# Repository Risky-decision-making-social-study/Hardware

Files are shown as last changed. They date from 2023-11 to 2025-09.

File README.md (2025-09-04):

# Hardware

This repository contains the design files and documentation for the "How does social context modulate risky decision-making in long-tailed macaques (Macaca fascicularis)? A research report on problematic issues with a repeated sampling from experience paradigm" project.

Fancy-Drawing

## Publication



## Online Viewer

You can view the design files in your browser using the online viewer.

<https://a360.co/31DxOK0>

## Manufacturing

The files for manufacturing can be found in the following folders:

+ STL/: Contains the STL files for 3D printing the parts.
+ Panels/: Contains the files for cutting the panels.
+ PDF/: Contains the files with specifications, turning and assembly instructions.

Alternatively, you can export all parts from the provided full assemblies with either the `ApparatusAssembly.step` or `ApparatusAssembly.f3z` files.

## Concept

For further discussion about the individual parts and modules, read the concept and implementation descriptions in the [concept folder](Concept/README.md).

## Bill of Materials

For a list of parts used in the construction of the Apparatuses in this project and a cost estimation, look at the [BOM.md file](BOM.md).

## License

This project is licensed under the MIT License - see the LICENSE.md file for details.

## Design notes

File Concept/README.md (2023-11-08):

# Hardware concept

## Carousel

The carousel is the component that is responsible for the reward distribution. Mechanically, the carousel is driven by a stepper motor that is connected to the carousel assembly via a gear train with a ratio of 18:5. This allows the motor to achieve an accuracy of 0.5° without microstepping when rotating the carousel, as calculated in [Table 1](#table_1). In addition, the carousel is equipped with an absolute magnetic encoder which allows it to determine the current absolute position of the carousel at any time after a one-time calibration. The encoder is located on the underside of the carrier plate and is mounted according to the data sheet of the AS5048A which is used in this application. Except for the mount plate, the carousel consists of only 3D-printed parts and is designed for production using the FDM printing process.

carousel figures

*Figure 1: Concept*

| Steps-Rotation                | Carousel |
| ----------------------------- | -------- |
| Compartments per Rotation     | 16       |
| Angle per Compartment         | 22,5°    |
| Gear Carousel Teeth           | 180      |
| Gear Stepper Teeth            | 50       |
| Stepper Angle per Compartment | 81°      |
| Stepper StepAngle             | 1,8°     |
| Steps per Compartment         | 45       |

*Table 1: Steps and rotational calculations of the square*

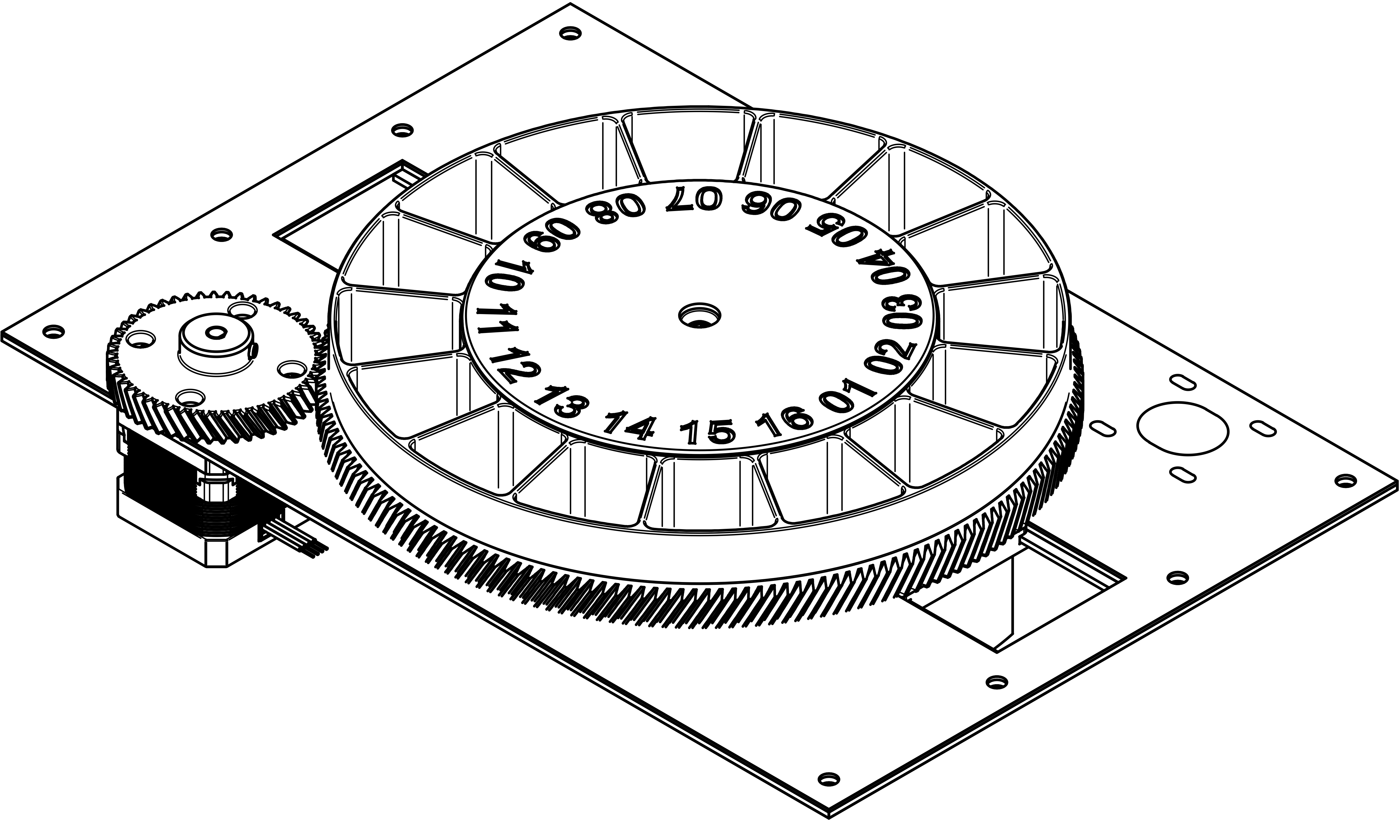
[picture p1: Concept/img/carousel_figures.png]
carousel figures


*Figure 2: Final Drawing*

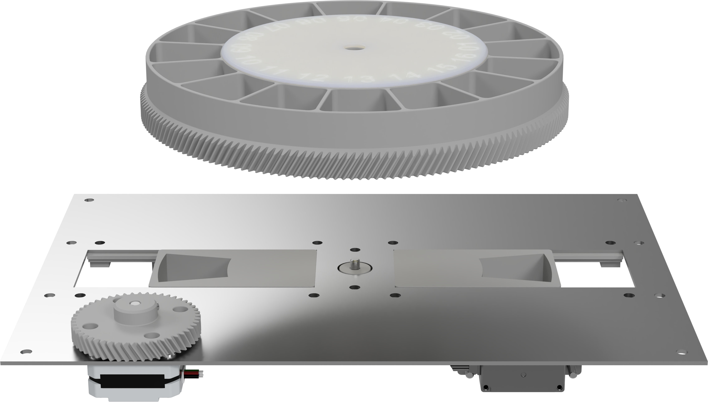
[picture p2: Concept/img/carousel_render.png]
carousel render


*Figure 3: Final Render*

## Frame

The main structure of the apparatuses is constructed out of aluminum extrusions, which allows for changes to the structure later on and are very easy to assemble. Additionally, they are very durable, which is a big advantage for a portable piece of hardware like this, as it can support the panels, allowing for weight savings on the paneling and even allows the apparatus to survive drops with ease.

fram_frame

*Figure 4: Frame*

## Lights

The illumination of the apparatuses is done by LED strips. A addressable lighting system based on addressable LEDs. Examples of the individual LED components are WS2812B, SK9822 and APA102C. These LED components are commonly sold as LED strips by the meter, which are suitable for use directly behind a diffuser, like the outer wall of the apparatuses, as shown in [Figure 5](#figure_5). In this concept, the signal light can be controlled virtually via the status light. For this purpose, a part of the status light LED strips is placed in a delimited area on the inside of the diffuser near the lever and switched on and off independently of the rest of the strip. The color of the signal light can also be changed afterwards.

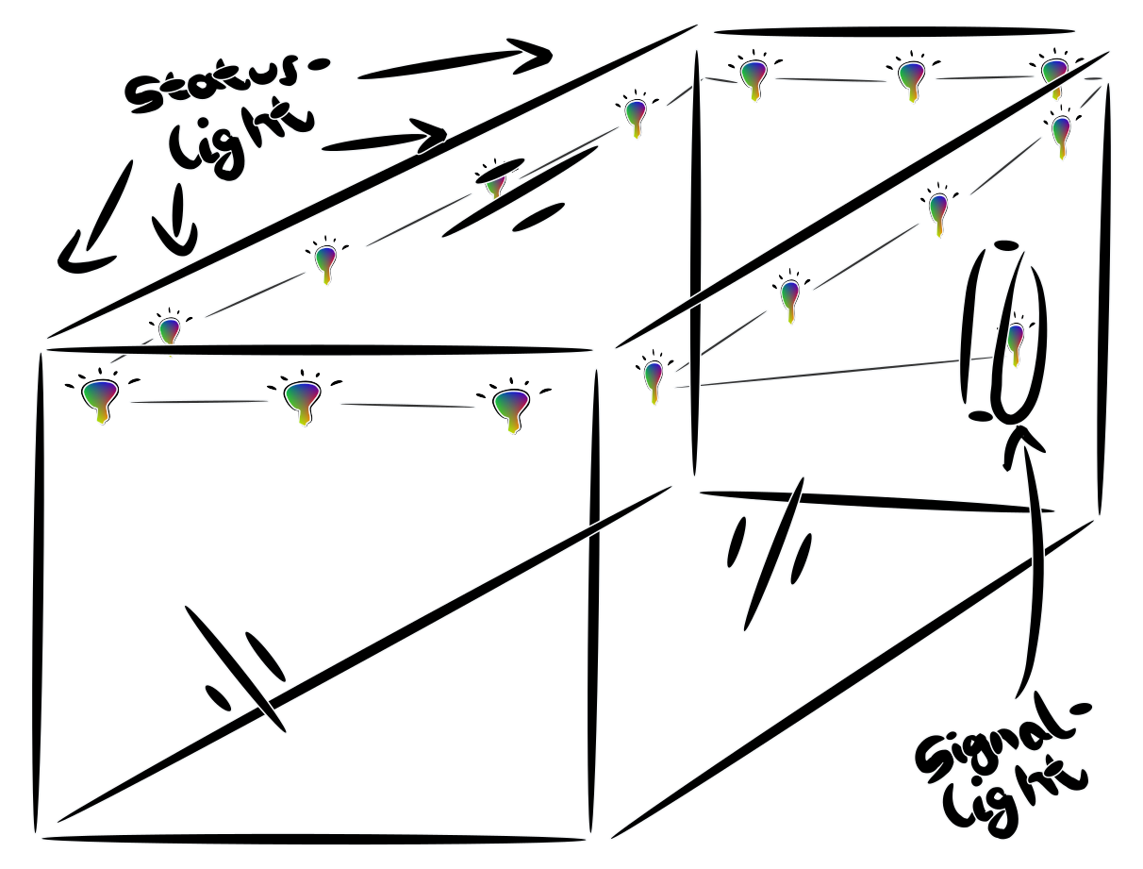
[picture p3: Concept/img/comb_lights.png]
comb_lights


*Figure 5: Lights*

## Lever

The lever is, as can be seen in [Figure 7](#figure_7), the mechanically most complex individual component of the apparatuses. It has a motorized locking system that prevents the lever from moving downward. It also has three sensors that detect touch, the states of the lever being fully pulled or fully up position. In addition, large parts of the lever are made of metal to withstand the mechanical stresses that occur when the lever is pulled by the subjects. These include the lever rod, the joint axis, and the parts of the locking device: ratchet wheel and pawl. In addition, a spring located in the lower part of the assembly ensures that the lever returns to the fully up position when no force is applied. Unfortunately, the lever is the most difficult to manufacture, as due to the high mechanical and environmental stress of the components, they have to be machined or cut out of stainless steel.

lever_ratchet

*Figure 6: Lever concept*

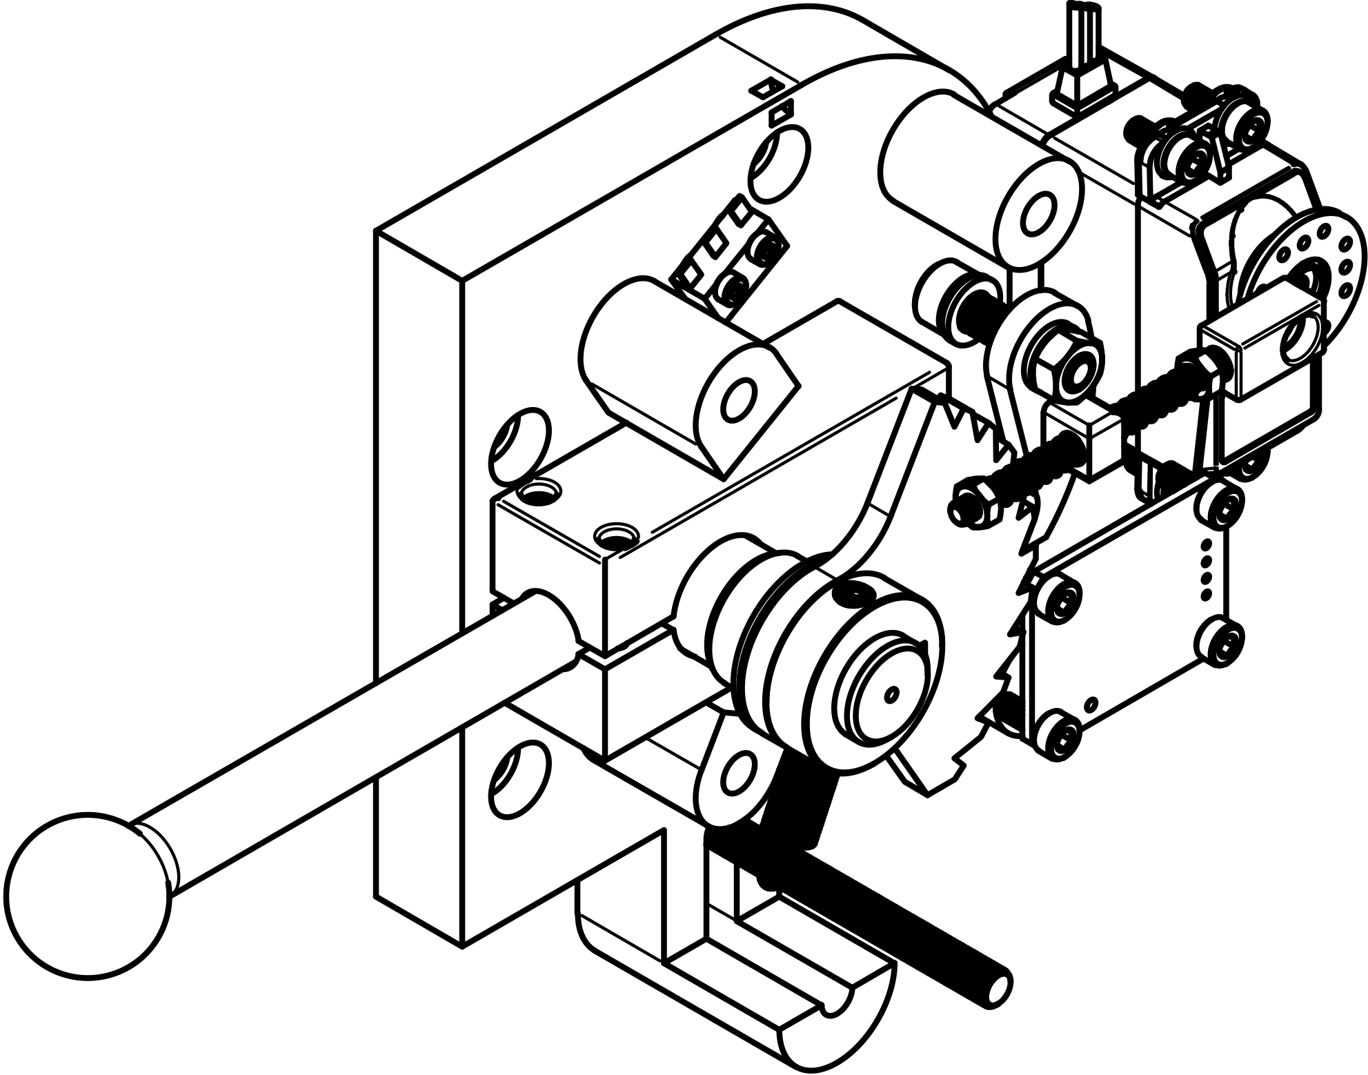
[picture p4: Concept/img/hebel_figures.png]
hebel_figures


*Figure 7: Open lever*

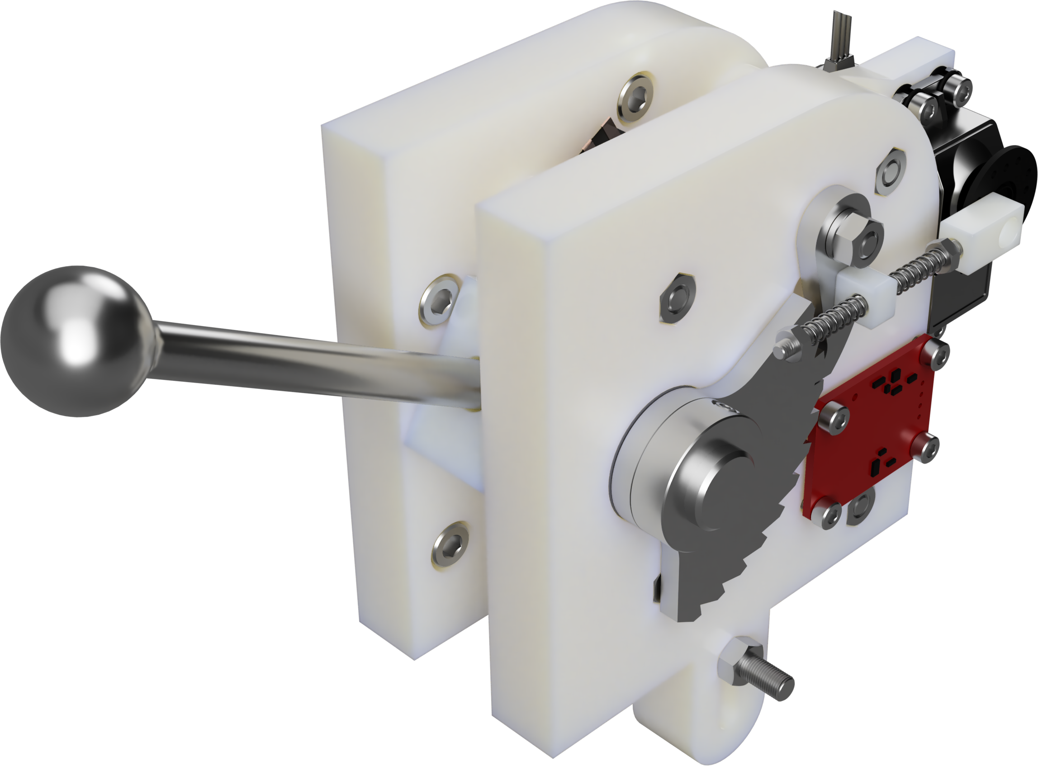
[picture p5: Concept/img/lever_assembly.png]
lever_assembly


*Figure 8: Render lever*

apparatus lever render

*Figure 9: Render lever in the apparatus*

## Hopper

The most important aspect when delivering rewards is the safety of the test subjects. For this reason, special care was taken in the design to ensure that the test subjects could not reach into the mechanical parts of the device. [Figure 10](#figure_10) shows the conceptual cross-section of the reward slide the test subjects interact with. The smallest distance between the walls is chosen so that a standard grape with an estimated maximum diameter of up to 20 mm can still fit through, but due to the chosen path that the reward must take through the chute, it is made as difficult as possible to reach around it. The 20 mm grape is an upper size estimate that was chosen to take into account most of the possible reward types available to the researchers.

Reward_chute_locked

*Figure 10: Concept of a monkey proof reward chute*

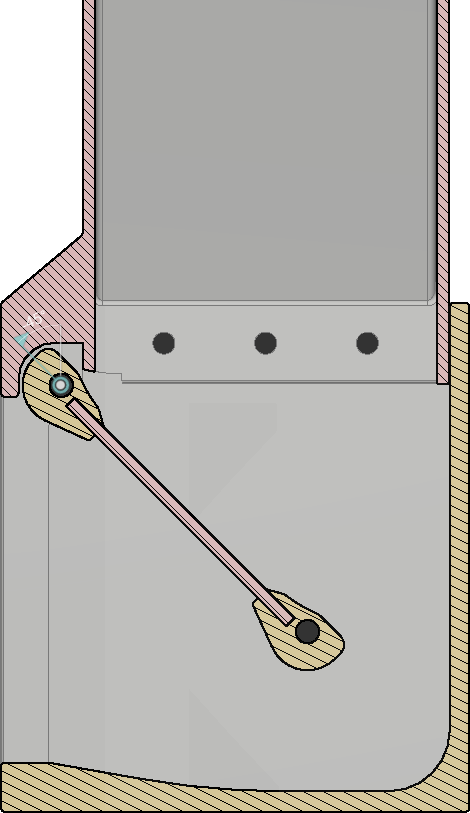
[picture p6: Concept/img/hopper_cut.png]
hopper_cut


*Figure 11: Section analysis of the final design*

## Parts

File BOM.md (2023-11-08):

| #   | Part Name                                                                                                                                                                      | Type / length mm                                                                                  | Number for two apparatuses | Estimated total amount for two apparatuses |
| --- | ------------------------------------------------------------------------------------------------------------------------------------------------------------------------------ | ------------------------------------------------------------------------------------------------- | -------------------------- | ------------------------------------------ |
| 1   | Grooved ball bearing                                                                                                                                                           | 8x16x5                                                                                            | 4                          | 0,00 €                                     |
| 2   | Screw DIN EN ISO 7380 - Pan head screw                                                                                                                                         | M2x5                                                                                              | 4                          | 0,00 €                                     |
| 3   | HAWA 1008234 Kaltgeräte Anschlusskabel Schwarz 5.00 m                                                                                                                          | Power cable                                                                                       | 2                          | 0,00 €                                     |
| 4   | LOCTITE 243 Medium Strength Threadlocker Adhesive Glue 50ml Bottle                                                                                                             | Screw locking varnish                                                                             | 2                          | 36,08 €                                    |
| 5   | ruthex Threaded Insert, Brass Threaded Bushings                                                                                                                                | 3D printing thread inserts                                                                        | 1                          | 27,99 €                                    |
| 6   | Nema 17 Bipolar 1.8deg 16Ncm (22.6oz.in) 1A 3.7V 42x42x20mm 4 Wires                                                                                                            | 17HS08-1004S                                                                                      | 6                          | 65,94 €                                    |
| 7   | BTF-LIGHTING SK9822 (similar to APA102C) Individually Addressable 16.5ft 5m 60 Pixels/LEDs/m 300 LEDs IP30 Non-Waterproof Black PCB Data and Clock Separately DC5V Full Colour | 5m (for both apparatuses)                                                                         | 1                          | 65,99 €                                    |
| 8   | 14-bit Magnetic Rotary Encoder IC                                                                                                                                              | AS5048                                                                                            | 4                          | 56,68 €                                    |
| 9   | Servo 180deg                                                                                                                                                                   | ROB-11965                                                                                         | 10                         | 109,50 €                                   |
| 10  | TMC2209 SILENTSTEPSTICK                                                                                                                                                        | (empty)                                                                                           | 12                         | 149,04 €                                   |
| 11  | DC Step Down Converter Buck Voltage Regulator 18-72V to 5V 6A 30W                                                                                                              | LED Voltage Supply                                                                                | 2                          | 46,50 €                                    |
| 12  | GST90A24-P1M                                                                                                                                                                   | AC/DC unit                                                                                        | 2                          | 56,36 €                                    |
| 13  | 1803277                                                                                                                                                                        | J2.1                                                                                              | 6                          | 4,20 €                                     |
| 14  | 1803578                                                                                                                                                                        | J2.2                                                                                              | 6                          | 12,18 €                                    |
| 15  | 12063A822JAT2A                                                                                                                                                                 | C5                                                                                                | 18                         | 8,28 €                                     |
| 16  | C3225X7R1H106M250AC                                                                                                                                                            | C2, C10                                                                                           | 8                          | 6,32 €                                     |
| 17  |                                                                                                                                                                                | C2, C10                                                                                           | 14                         | 11,06 €                                    |
| 18  | CC0805KRX7R7BB104                                                                                                                                                              | C6, C9                                                                                            | 8                          | 0,80 €                                     |
| 19  |                                                                                                                                                                                | C6, C9                                                                                            | 14                         | 1,40 €                                     |
| 20  | CG0603MLC-05LE                                                                                                                                                                 | D3                                                                                                | 6                          | 1,98 €                                     |
| 21  | CG0603MLC-24LE                                                                                                                                                                 | D2                                                                                                | 6                          | 1,98 €                                     |
| 22  |                                                                                                                                                                                | D2                                                                                                | 12                         | 3,84 €                                     |
| 23  | CG0603MLC-3.3LE                                                                                                                                                                | D4-D15                                                                                            | 28                         | 9,24 €                                     |
| 24  |                                                                                                                                                                                | D4, D5, D6, D7, D8, D9, D10, D11, D12, D13, D14, D15, D16, D17, D18, D19, D20, D21, D22, D23, D24 | 62                         | 13,04 €                                    |
| 25  | CL21A106KQCLRNC                                                                                                                                                                | C1                                                                                                | 18                         | 1,62 €                                     |
| 26  | CL21B105KOFNNNG                                                                                                                                                                | C8                                                                                                | 18                         | 1,44 €                                     |
| 27  | CL21C100JBANNNC                                                                                                                                                                | C3                                                                                                | 18                         | 1,44 €                                     |
| 28  | CRCW080510K0FKEAC                                                                                                                                                              | R3, R4                                                                                            | 8                          | 0,64 €                                     |
| 29  |                                                                                                                                                                                | R3, R4, R16, R21, R22, R25, R26                                                                   | 24                         | 1,92 €                                     |
| 30  | CRCW080510K2FKEA                                                                                                                                                               | R14                                                                                               | 18                         | 1,44 €                                     |
| 31  | CRCW08051K96FKEA                                                                                                                                                               | R15                                                                                               | 18                         | 1,44 €                                     |
| 32  | CRCW0805220RFKEAC                                                                                                                                                              | R5-R10                                                                                            | 16                         | 1,28 €                                     |
| 33  |                                                                                                                                                                                | R5, R6, R7, R8, R9, R10, R11, R12, R17, R18, R19, R20                                             | 34                         | 2,72 €                                     |
| 34  | CRCW08054K70FKEAC                                                                                                                                                              | R1, R2                                                                                            | 8                          | 0,64 €                                     |
| 35  |                                                                                                                                                                                | R1, R2                                                                                            | 14                         | 1,12 €                                     |
| 36  | CRCW080560K4FKEA                                                                                                                                                               | R13                                                                                               | 18                         | 1,44 €                                     |
| 37  | GRM2165C1H102JA01J                                                                                                                                                             | C4                                                                                                | 18                         | 2,52 €                                     |
| 38  | GRM32ER61C476KE15L                                                                                                                                                             | C7, C11, C12                                                                                      | 10                         | 9,60 €                                     |
| 39  |                                                                                                                                                                                | C7, C11, C12                                                                                      | 6                          | 5,76 €                                     |
| 40  | NCP164CSN330T1G                                                                                                                                                                | U3                                                                                                | 8                          | 4,16 €                                     |
| 41  | PCA9685PW,118                                                                                                                                                                  | U1                                                                                                | 8                          | 15,28 €                                    |
| 42  | PRT-14017                                                                                                                                                                      | J1                                                                                                | 8                          | 13,20 €                                    |
| 43  | SBRD10200TR                                                                                                                                                                    | D1                                                                                                | 8                          | 3,20 €                                     |
| 44  | TPS54531DDAR                                                                                                                                                                   | U2                                                                                                | 8                          | 10,56 €                                    |
| 45  | TSW-150-07-T-S                                                                                                                                                                 | J3-J14                                                                                            | 8                          | 16,16 €                                    |
| 46  | Omron Electronics Inc-EMC Div D2F-5L                                                                                                                                           | Microswitch                                                                                       | 4                          | 9,44 €                                     |
| 47  | DIN 35 – Hutschiene                                                                                                                                                            | 35x220mm                                                                                          | 2                          | 36,50 €                                    |
| 48  | EHRJ45P6S                                                                                                                                                                      | RJ45 Panel Mount                                                                                  | 2                          | 21,48 €                                    |
| 49  | PJ-065B                                                                                                                                                                        | Connector Panel ID 2,50mm, AD 5,50mm, L 10.70mm                                                   | 4                          | 7,28 €                                     |
| 50  | SEN-12041                                                                                                                                                                      | Chip: capacitive sensor                                                                           | 3                          | 17,61 €                                    |
| 51  | 150080RS75000                                                                                                                                                                  | D25                                                                                               | 12                         | 1,80 €                                     |
| 52  | CG0603MLC-05E                                                                                                                                                                  | D3                                                                                                | 12                         | 4,80 €                                     |
| 53  | CRCW0603100RFKEAC                                                                                                                                                              | R23, R24, R27, R28, R29, R30                                                                      | 22                         | 1,76 €                                     |
| 54  | EEE-FT1V101AP                                                                                                                                                                  | C13, C14                                                                                          | 14                         | 5,88 €                                     |
| 55  | RC0805FR-0749R9L                                                                                                                                                               | R31                                                                                               | 12                         | 0,96 €                                     |
| 56  | CL10B103KB8NNNC                                                                                                                                                                | C15, C16                                                                                          | 12                         | 0,96 €                                     |
| 57  | SN74LVC2T45DCUR                                                                                                                                                                | U4                                                                                                | 4                          | 1,92 €                                     |
| 58  | Trägerplatte (Alu/Pertinax)                                                                                                                                                    | 320x220x3                                                                                         | 4                          | 0,00 €                                     |
| 59  | Aluprofil 20x20 I-Typ Nut 5                                                                                                                                                    | 280 mm                                                                                            | 14                         | 12,76 €                                    |
| 60  |                                                                                                                                                                                | 320 mm                                                                                            | 8                          | 8,33 €                                     |
| 61  |                                                                                                                                                                                | 490mm                                                                                             | 12                         | 19,14 €                                    |
| 62  |                                                                                                                                                                                | 225 mm                                                                                            | 8                          | 5,86 €                                     |
| 63  | Nutenstein mit Steg I-Typ Nut 5 {[}M5{]}                                                                                                                                       | M5                                                                                                | 540                        | 98,06 €                                    |
| 64  | Schraube DIN EN ISO 7380 - Linsenkopfschraube                                                                                                                                  | M3x8                                                                                              | 16                         | 3,08 €                                     |
| 65  |                                                                                                                                                                                | M4x8                                                                                              | 32                         | 12,47 €                                    |
| 66  |                                                                                                                                                                                | M5x16                                                                                             | 48                         | 18,70 €                                    |
| 67  |                                                                                                                                                                                | M5x35                                                                                             | 4                          | 1,56 €                                     |
| 68  |                                                                                                                                                                                | M5x8                                                                                              | 70                         | 27,27 €                                    |
| 69  | Igus Gleitlager mit Bund GFM-1618-09                                                                                                                                           | Slide bearing                                                                                     | 6                          | 14,66 €                                    |
| 70  | Präzisionswelle Stahl Ø16mm                                                                                                                                                    | 500 mm                                                                                            | 1                          | 3,23 €                                     |
| 71  | Senkschraube mit Innensechskant nach DIN 7991                                                                                                                                  | M5x16                                                                                             | 6                          | 2,34 €                                     |
| 72  | M5 Gewindestange DIN 976 Stahl, 1000mm                                                                                                                                         | Threaded rod                                                                                      | 1                          | 1,19 €                                     |
| 73  | Mutter DIN 934                                                                                                                                                                 | M5                                                                                                | 16                         | 4,72 €                                     |
| 74  | Stahlwinkel 20 verzinkt                                                                                                                                                        | 20x20 mm                                                                                          | 36                         | 36,11 €                                    |
| 75  | Gewindestange   60mm                                                                                                                                                           | M5                                                                                                | 2                          |                                            |
| 76  | XAL6060-562MEB                                                                                                                                                                 | L1                                                                                                | 6                          | 15,00 €                                    |
| 77  | Raspberry Pi RPI4-MODBP-4GB-BULK                                                                                                                                               | Single Board Computer                                                                             | 2                          | 117,50 €                                   |
| 78  | Digitus RJ45 Network cable, patch cable CAT 5e SF/UTP 0.50 m Green                                                                                                             | 0.5m Patch Cable                                                                                  | 4                          | 11,96 €                                    |
| 79  | Renkforce RJ45 Network cable, patch cable CAT 6A S/FTP 10.00 m Grey ultra flexible, gold plated connectors                                                                     | 10m Patch Cable                                                                                   | 2                          | 37,98 €                                    |
| 80  | TP-LINK Network switch 5 ports                                                                                                                                                 | NetworkSwitch                                                                                     | 1                          | 21,99 €                                    |
| 81  | Ultimaker Filament PA (Polyamid) 2.85 mm Schwarz 750 g                                                                                                                         | 3D printing Nylon                                                                                 | 2                          | 126,62 €                                   |
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

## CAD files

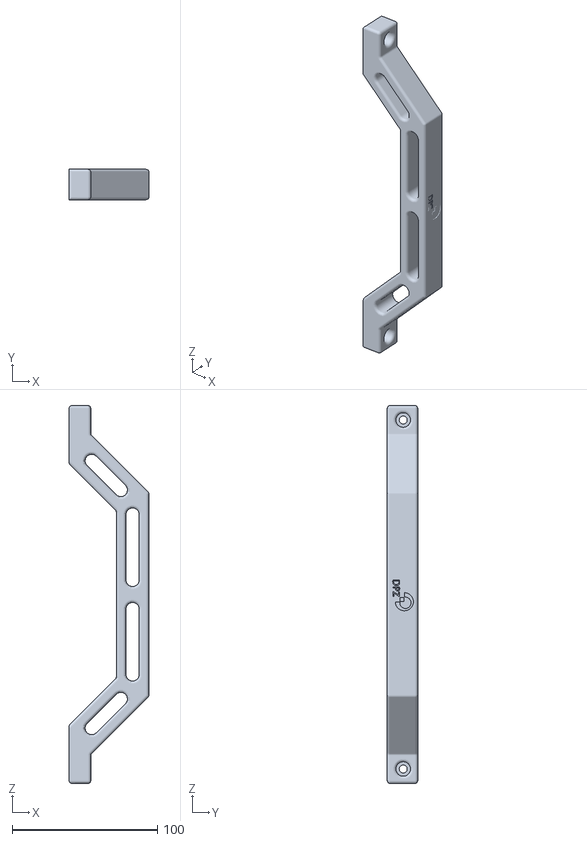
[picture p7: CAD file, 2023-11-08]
STL/AparatusAssembly_Handle.stl
55.0 x 21.0 x 260.0

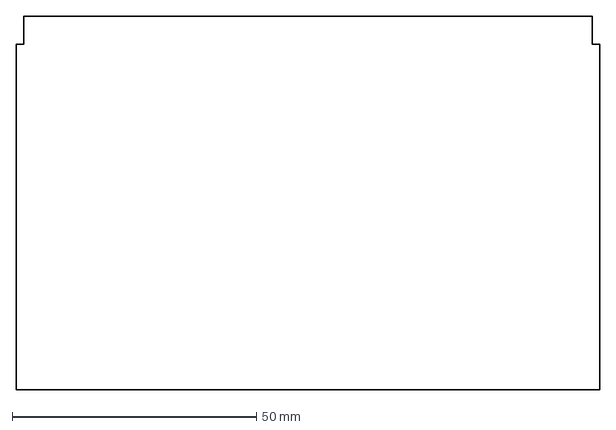
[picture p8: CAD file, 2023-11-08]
STL/ApparatusAssembly_Hopper/ApparatusAssembly_Hopper_Door_Short.dxf
119.5 x 76.5 mm

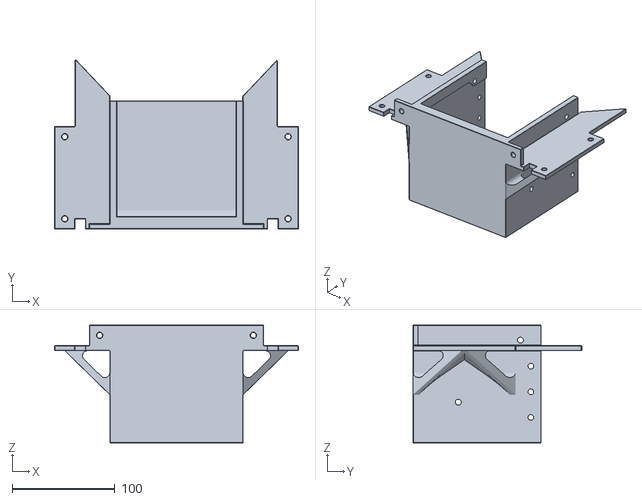
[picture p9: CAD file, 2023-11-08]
STL/ApparatusAssembly_Hopper/BottomPart.stl
238.0 x 164.9 x 115.0

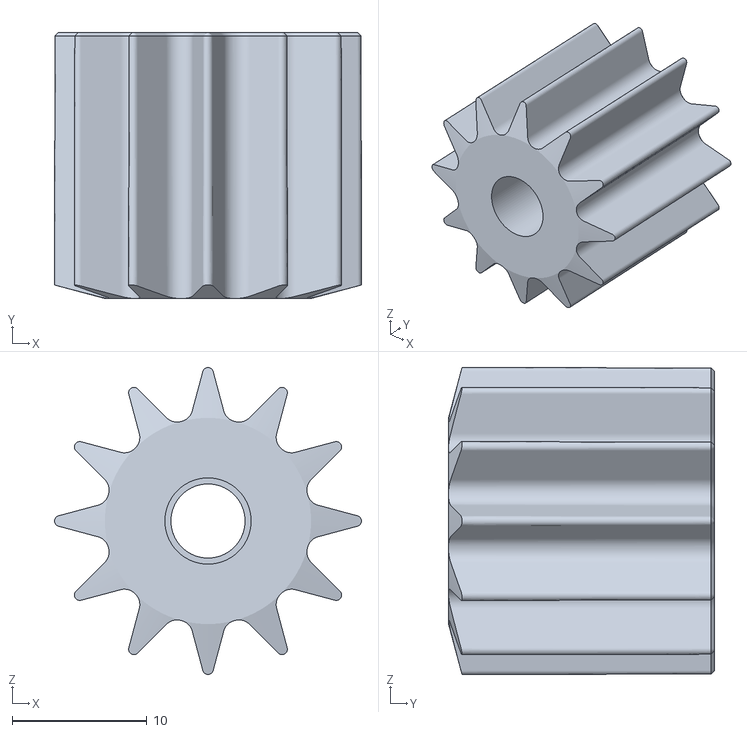
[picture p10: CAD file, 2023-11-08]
STL/Carousel_Assembly/Carousel_RotaryAssembly/Attacher.stl
22.8 x 19.8 x 22.8

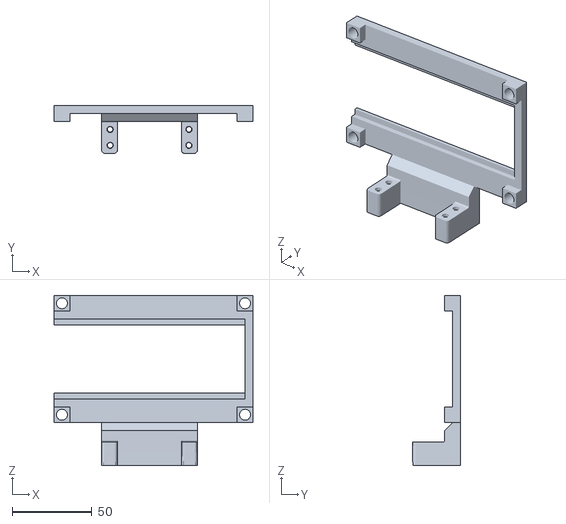
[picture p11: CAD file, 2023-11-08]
STL/Carousel_Assembly/Carousel_sliding-door/Rail.stl
125.0 x 30.0 x 107.0

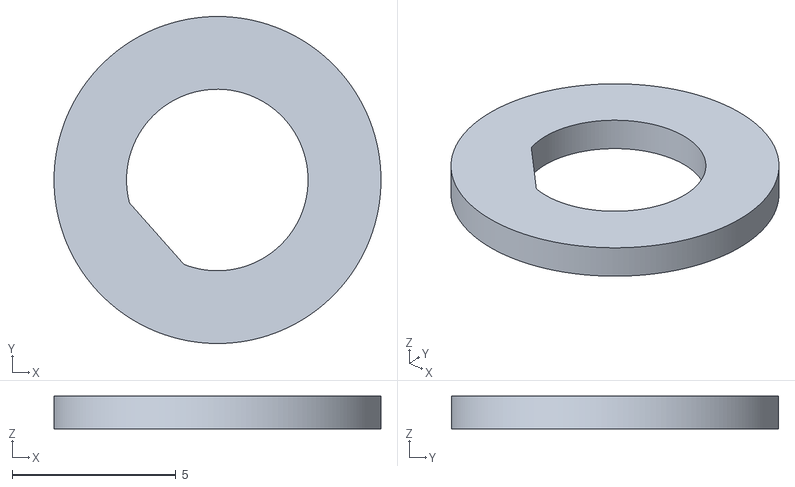
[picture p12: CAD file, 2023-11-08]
STL/Carousel_Assembly/Carousel_StepperAssembly/Spacer.stl
10.00 x 10.00 x 1.00

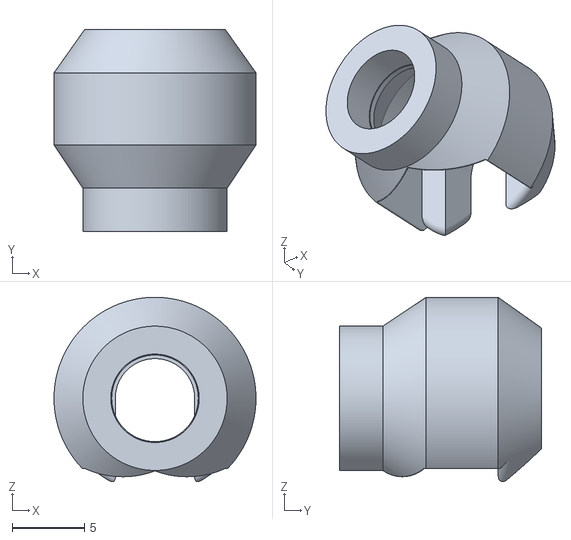
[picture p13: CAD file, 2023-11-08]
STL/Carousel_Assembly/MagnetMount.stl
14.0 x 14.0 x 12.8

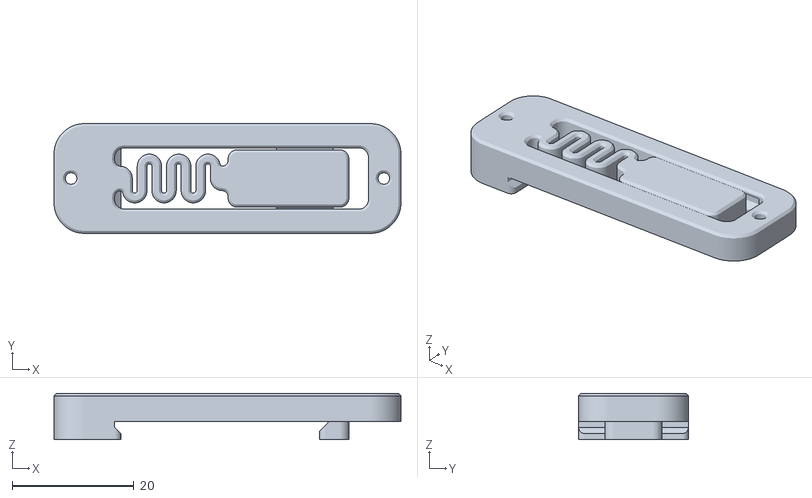
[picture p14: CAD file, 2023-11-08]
STL/ElectronicsRail/BracketRailMount.stl
56.9 x 18.0 x 7.60

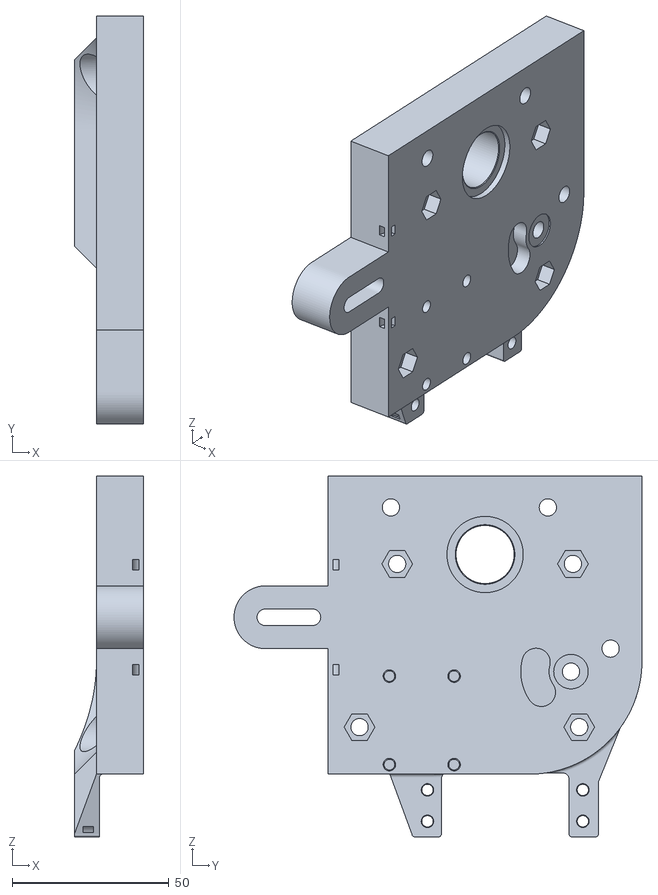
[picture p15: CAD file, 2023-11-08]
STL/LeverAssembly/Housing/Hebel_Plate_R.stl
22.0 x 130.0 x 115.0

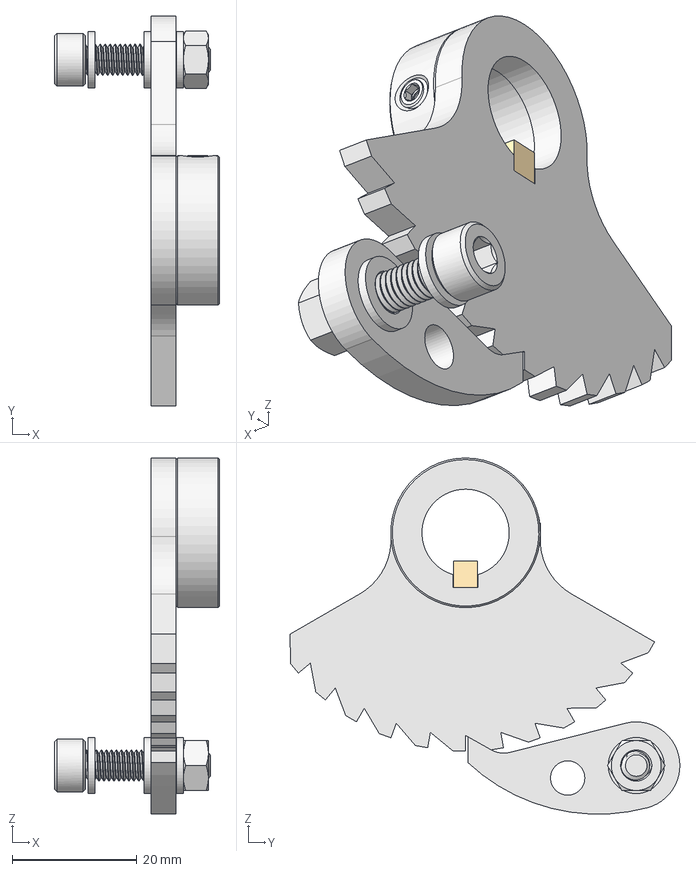
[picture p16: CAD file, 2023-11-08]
STL/LeverAssembly/KlinkenSperrung.step
26.5 x 62.5 x 57.1 mm
Sperrad
Klinke
Passfeder
M4x5 - DIN 914 - 91217A110
M5x20 - DIN 912 - 91292A128
M5 Nut - DIN 934 - 91828A241
MessingLager
M5x1mm OD 9mm Washer - DIN433 - 98690A112 x 3

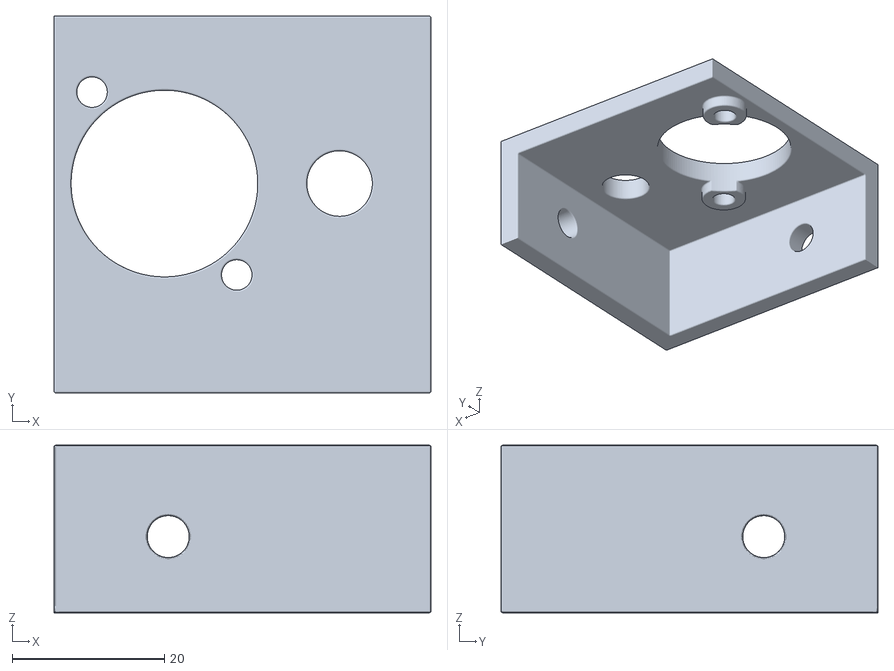
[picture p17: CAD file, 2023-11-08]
STL/PlugInterface.stl
49.5 x 49.5 x 22.0

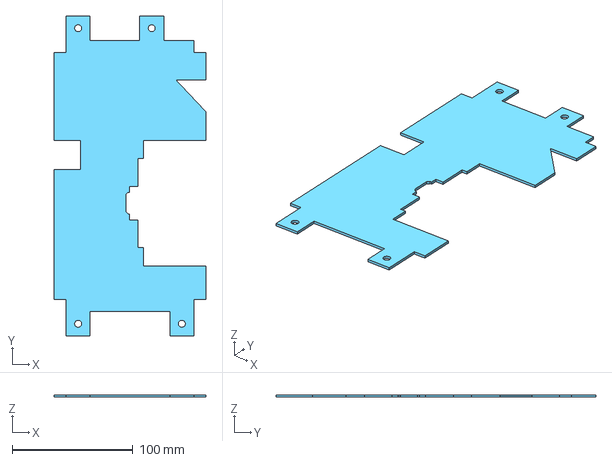
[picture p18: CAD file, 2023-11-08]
Panels/FrontInnerSide_Lever.step
126.0 x 265.0 x 2.00 mm

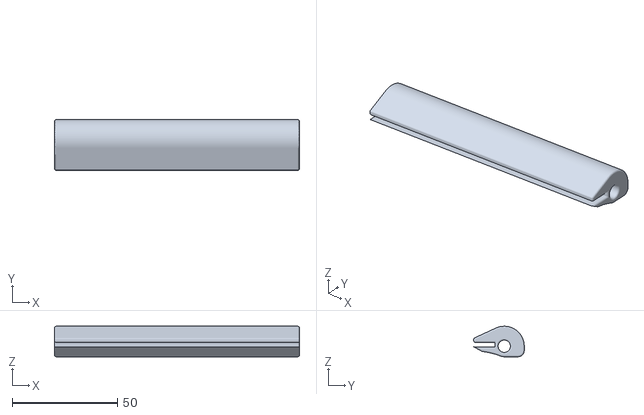
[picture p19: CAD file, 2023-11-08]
STL/ApparatusAssembly_Hopper/Hinge.stl
116.2 x 24.0 x 14.5

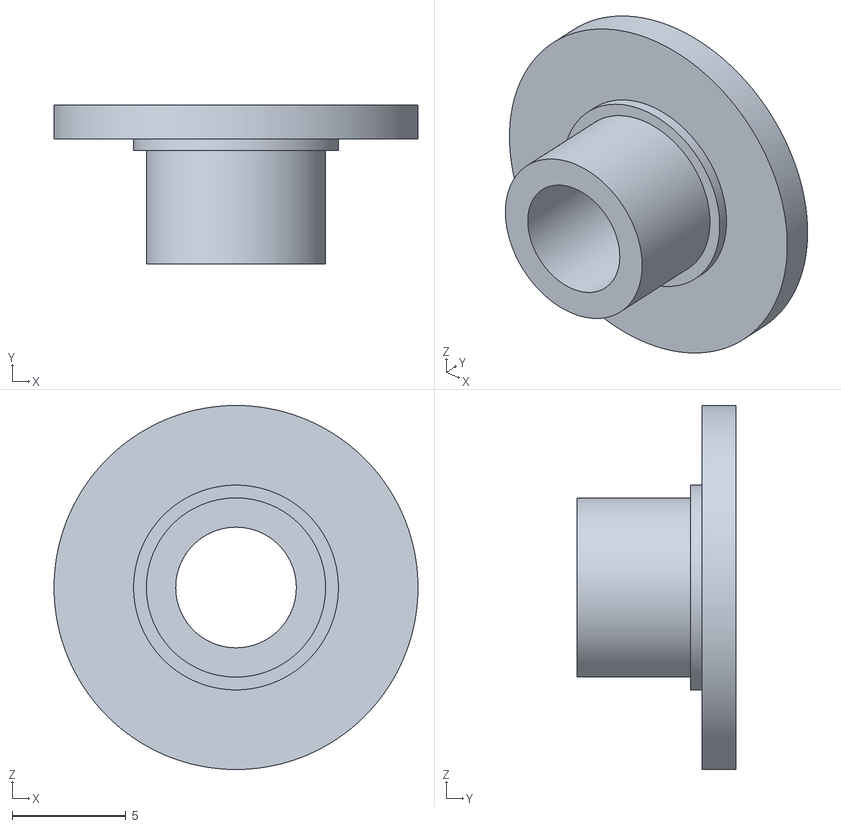
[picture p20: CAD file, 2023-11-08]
STL/Carousel_Assembly/AxisTranslator.stl
16.0 x 7.00 x 16.0

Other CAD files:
Panels/FrontOuterHuman.step
STL/Carousel_Assembly/Carousel_sliding-door/Car.stl
STL/ElectronicsRail/RPIBracket.stl
STL/Feet(Mirror).stl
Panels/Carousel_MountPlate.dxf
Panels/Carousel_MountPlate.step
Panels/FontInnerSide.step
Panels/FrontInnerSide.dxf
Panels/FrontInnerSide_Electric.dxf
Panels/FrontInnerSide_Electric.step
Panels/FrontInnerSide_Lever.dxf
Panels/FrontOuterHuman.dxf
Panels/FrontOuterMonkey.dxf
Panels/FrontOuterMonkey.step
Panels/FrontTopInner.dxf
Panels/FrontTopInner.step
Panels/ProtectionPanel.dxf
Panels/ProtectionPanel.step
Panels/SideInner.dxf
Panels/SideInner.step
Panels/SideOuter.dxf
Panels/SideOuter.step
Panels/TopBottomOuter.dxf
Panels/TopBottomOuter.step
STL/ApparatusAssembly_Hopper/Cover.stl
STL/ApparatusAssembly_Hopper/TopPart.stl
STL/Carousel_Assembly/Carousel_Joint.stl
STL/Carousel_Assembly/Carousel_sliding-door/Spur Gear (25 teeth).stl
STL/Feet.stl
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

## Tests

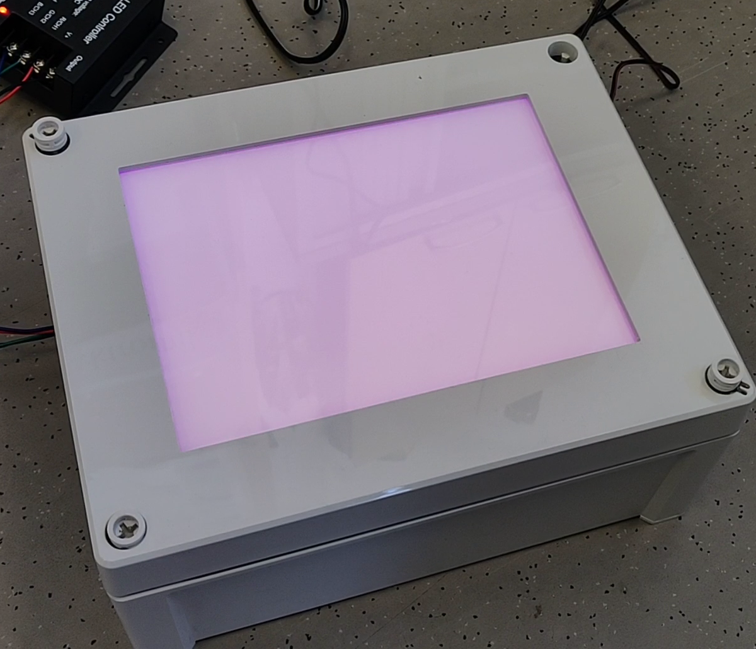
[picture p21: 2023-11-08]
Concept/img/LightTest/LightTest_02.png

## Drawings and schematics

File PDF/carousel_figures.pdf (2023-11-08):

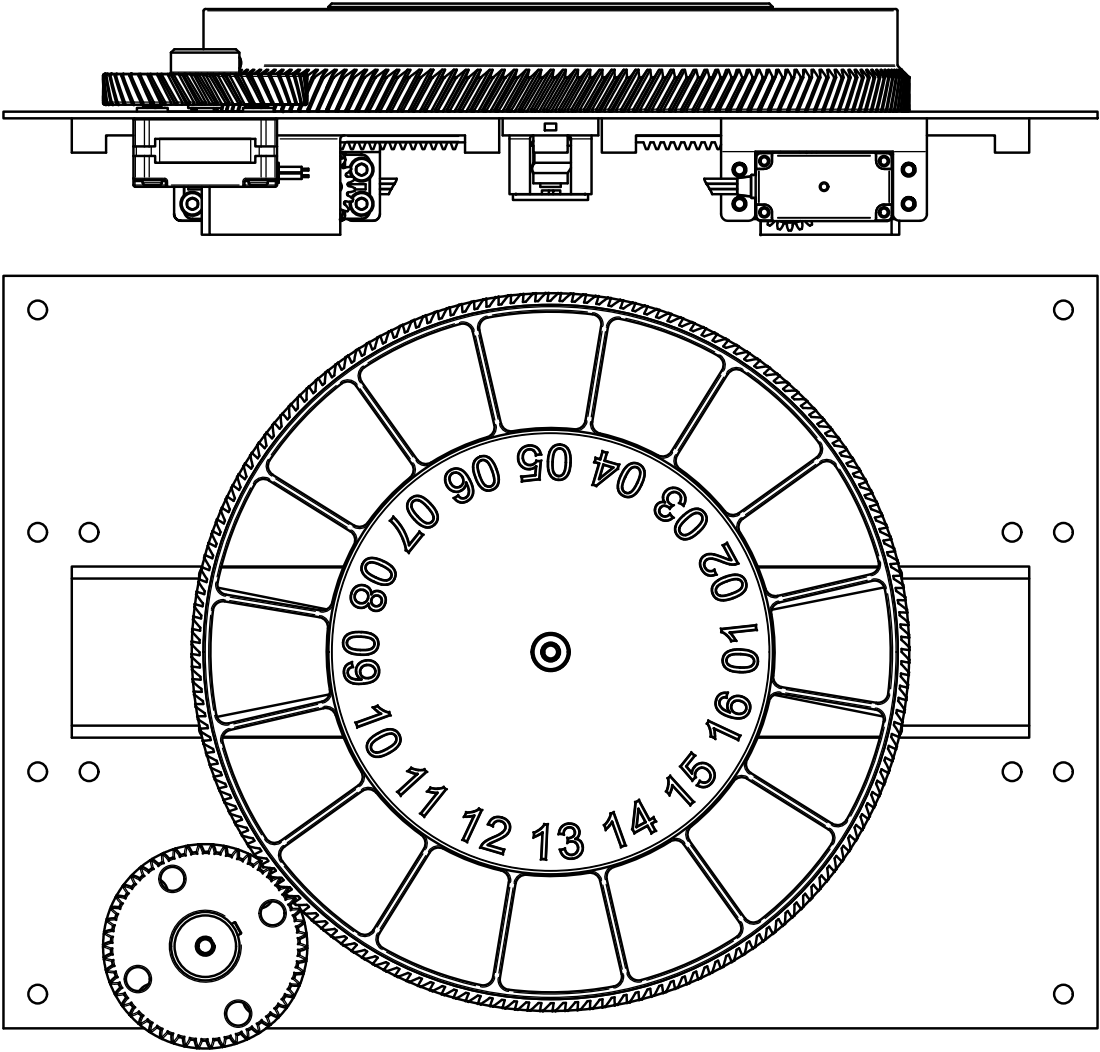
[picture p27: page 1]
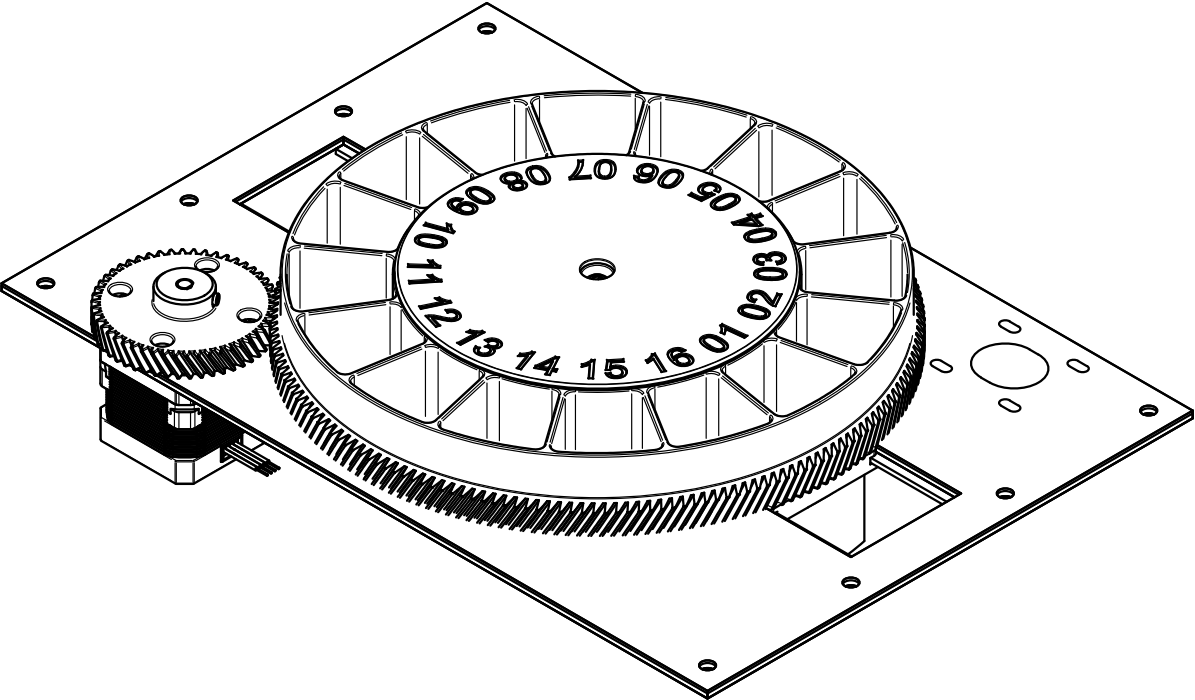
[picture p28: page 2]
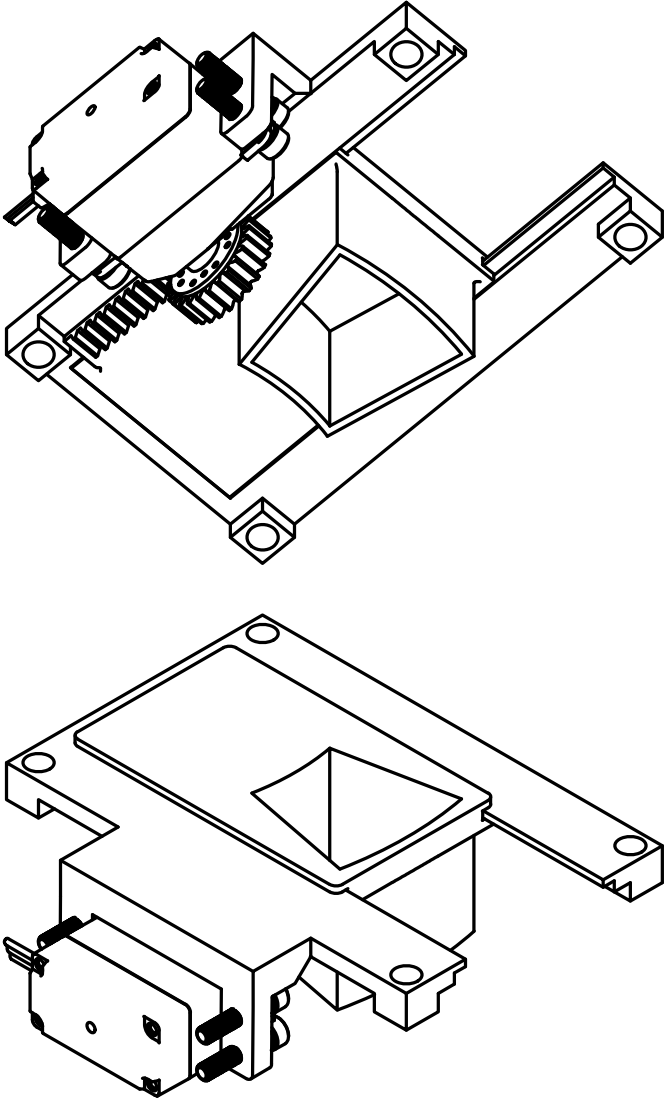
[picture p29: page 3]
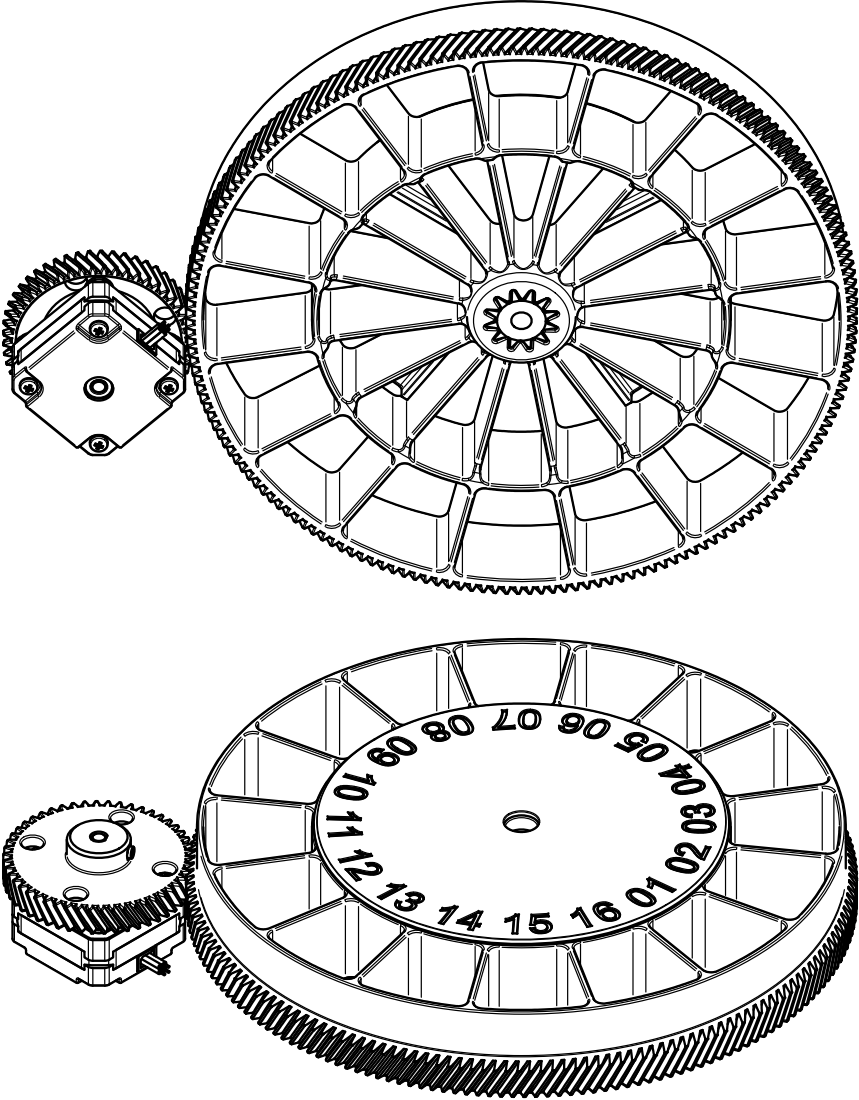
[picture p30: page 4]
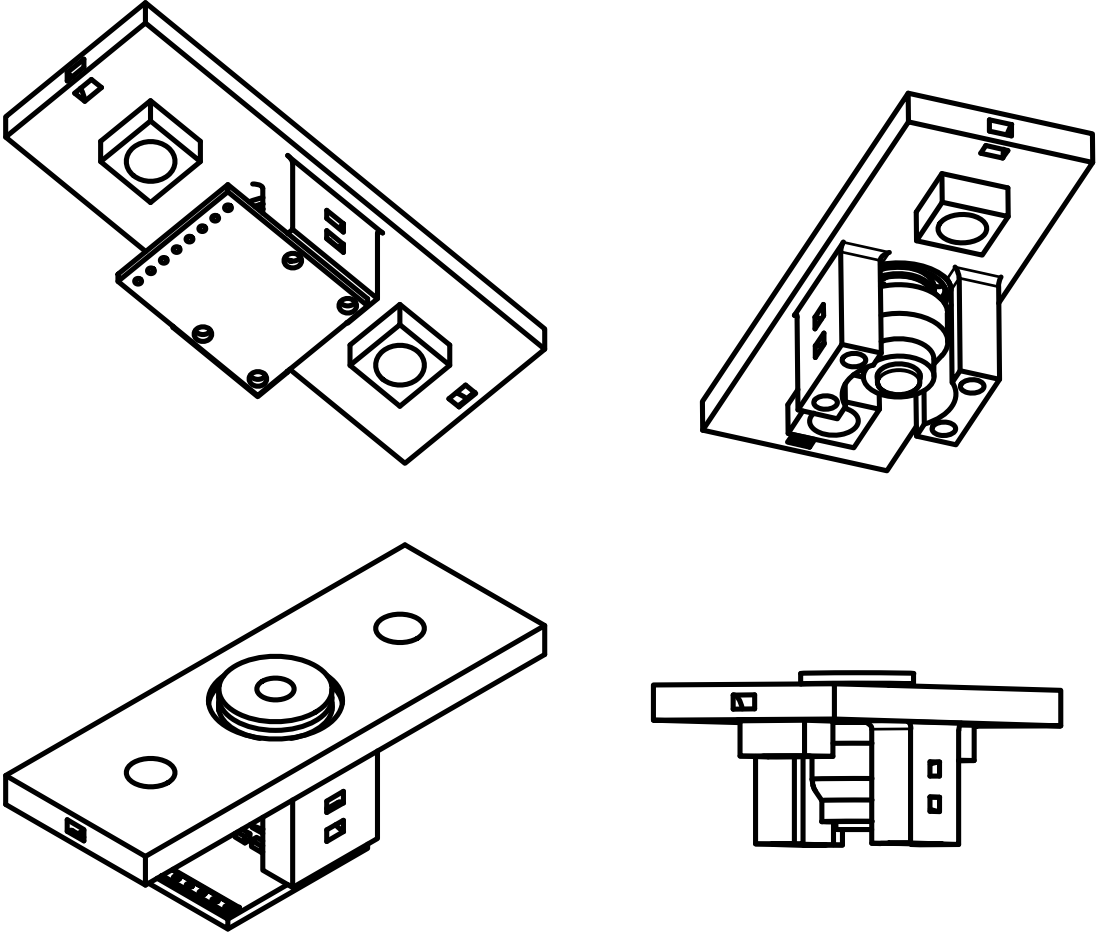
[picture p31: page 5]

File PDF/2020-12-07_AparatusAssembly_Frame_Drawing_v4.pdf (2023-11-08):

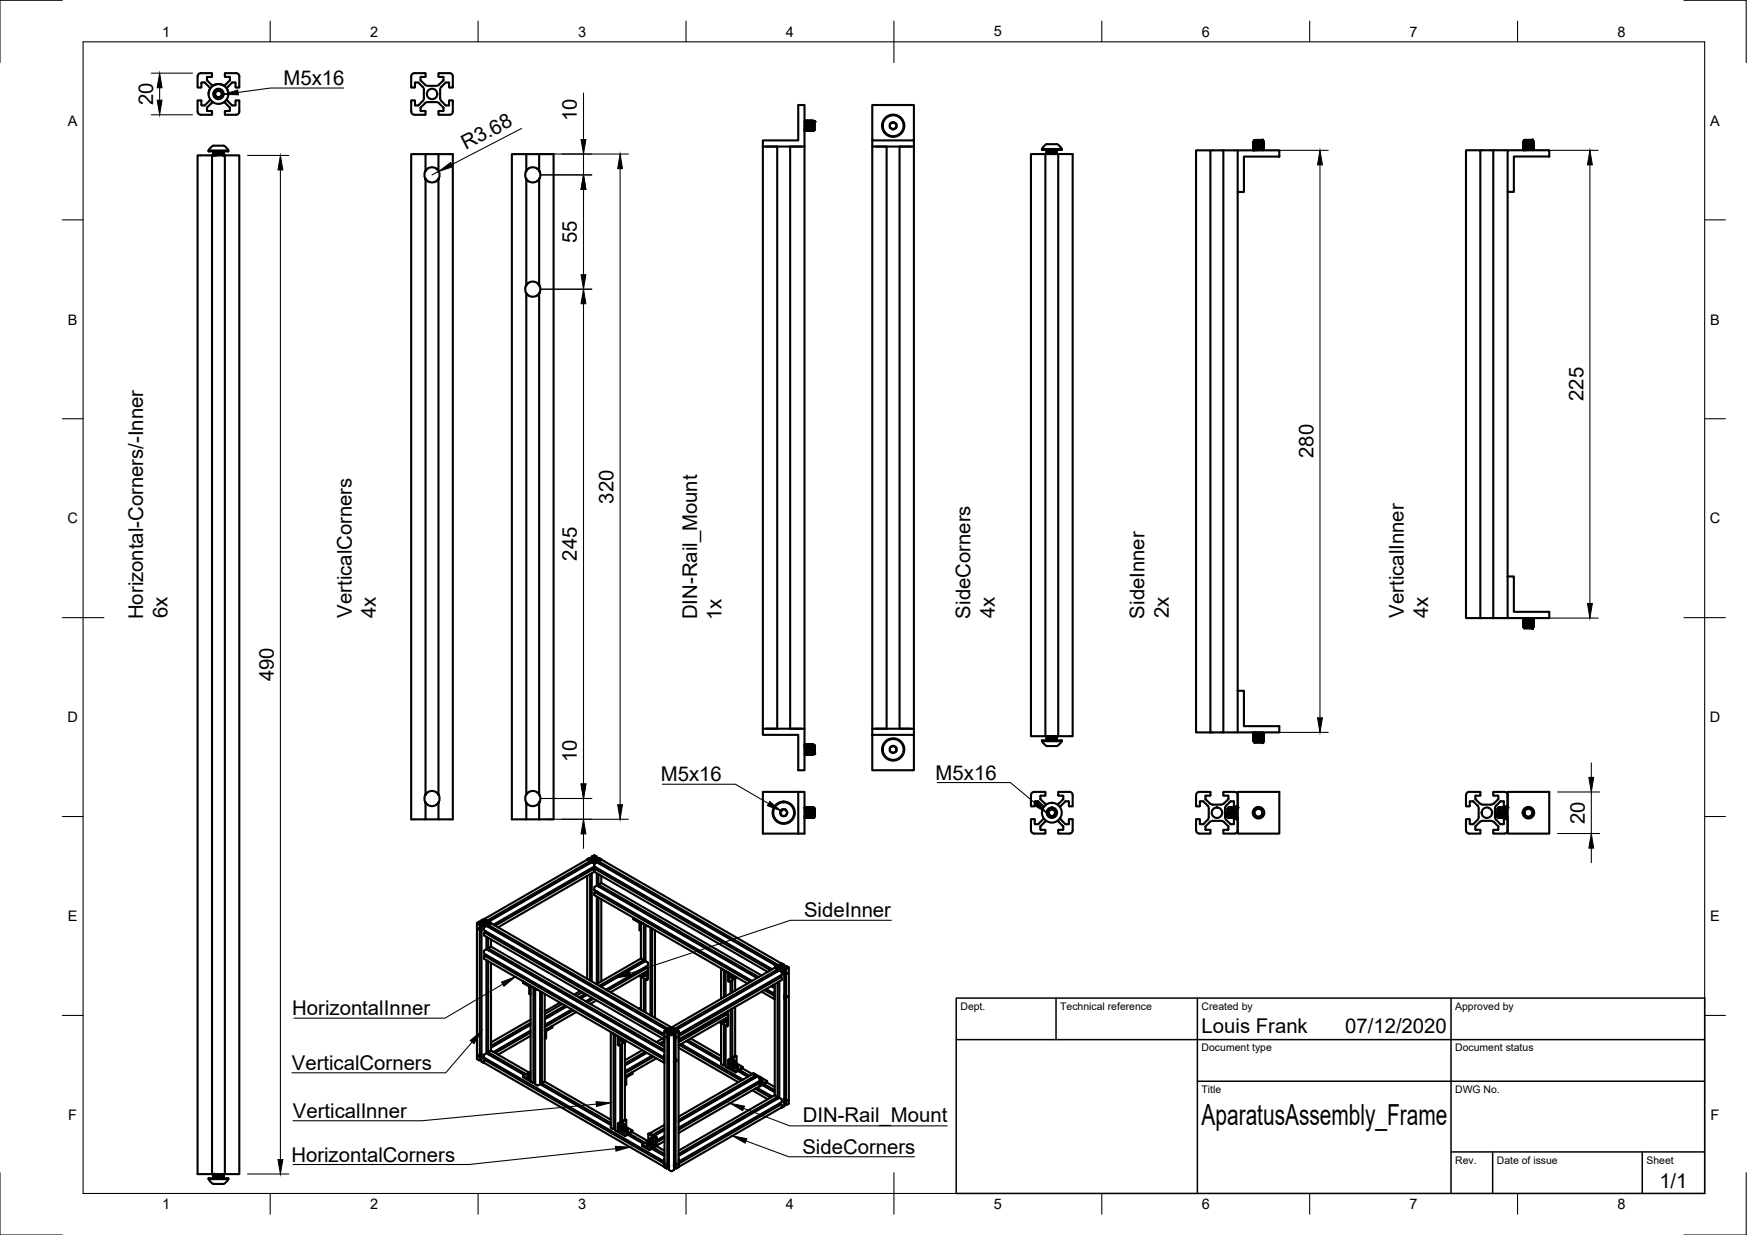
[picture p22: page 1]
Louis Frank Horizontal-Corners/-Inner 6x; VerticalCorners 4x; R3.68 DIN-Rail_Mount 1x; SideCorners 4x; SideInner 2x; VerticalInner 4x

Dept. | Technical reference | Created by 07/12/2020 | Approved by

Document type | Document status

Title AparatusAssembly_Frame | DWG No.

Rev. | Date of issue | Sheet 1/1

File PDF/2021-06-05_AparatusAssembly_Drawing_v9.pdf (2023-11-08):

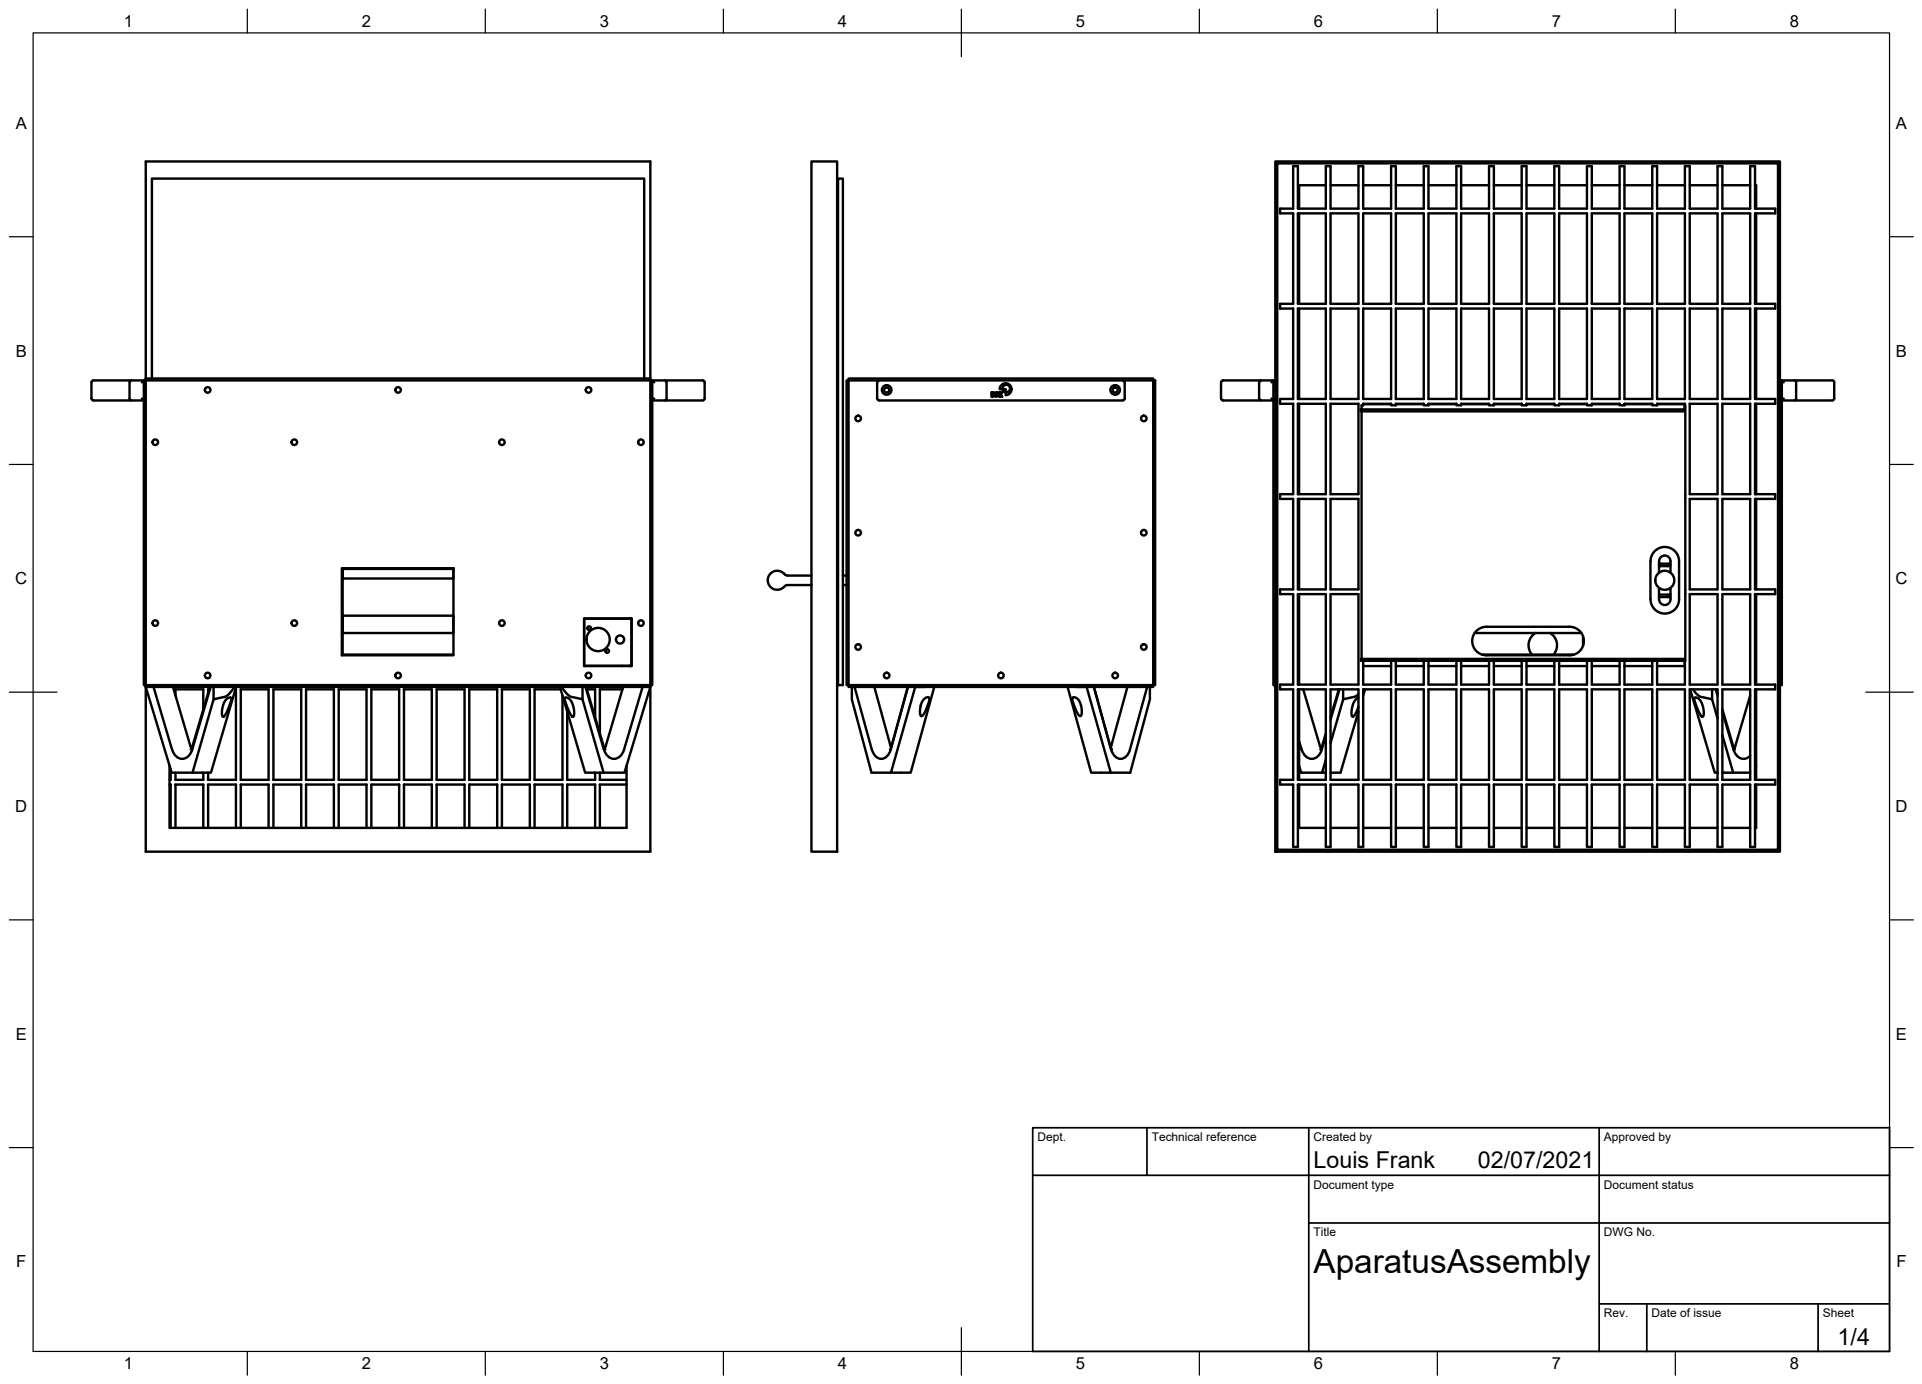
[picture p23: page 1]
Title; DWG No.; Rev.; Date of issue; Sheet

Dept. | Technical reference | Created by Louis Frank 02/07/2021 | Approved by

Document type | Document status

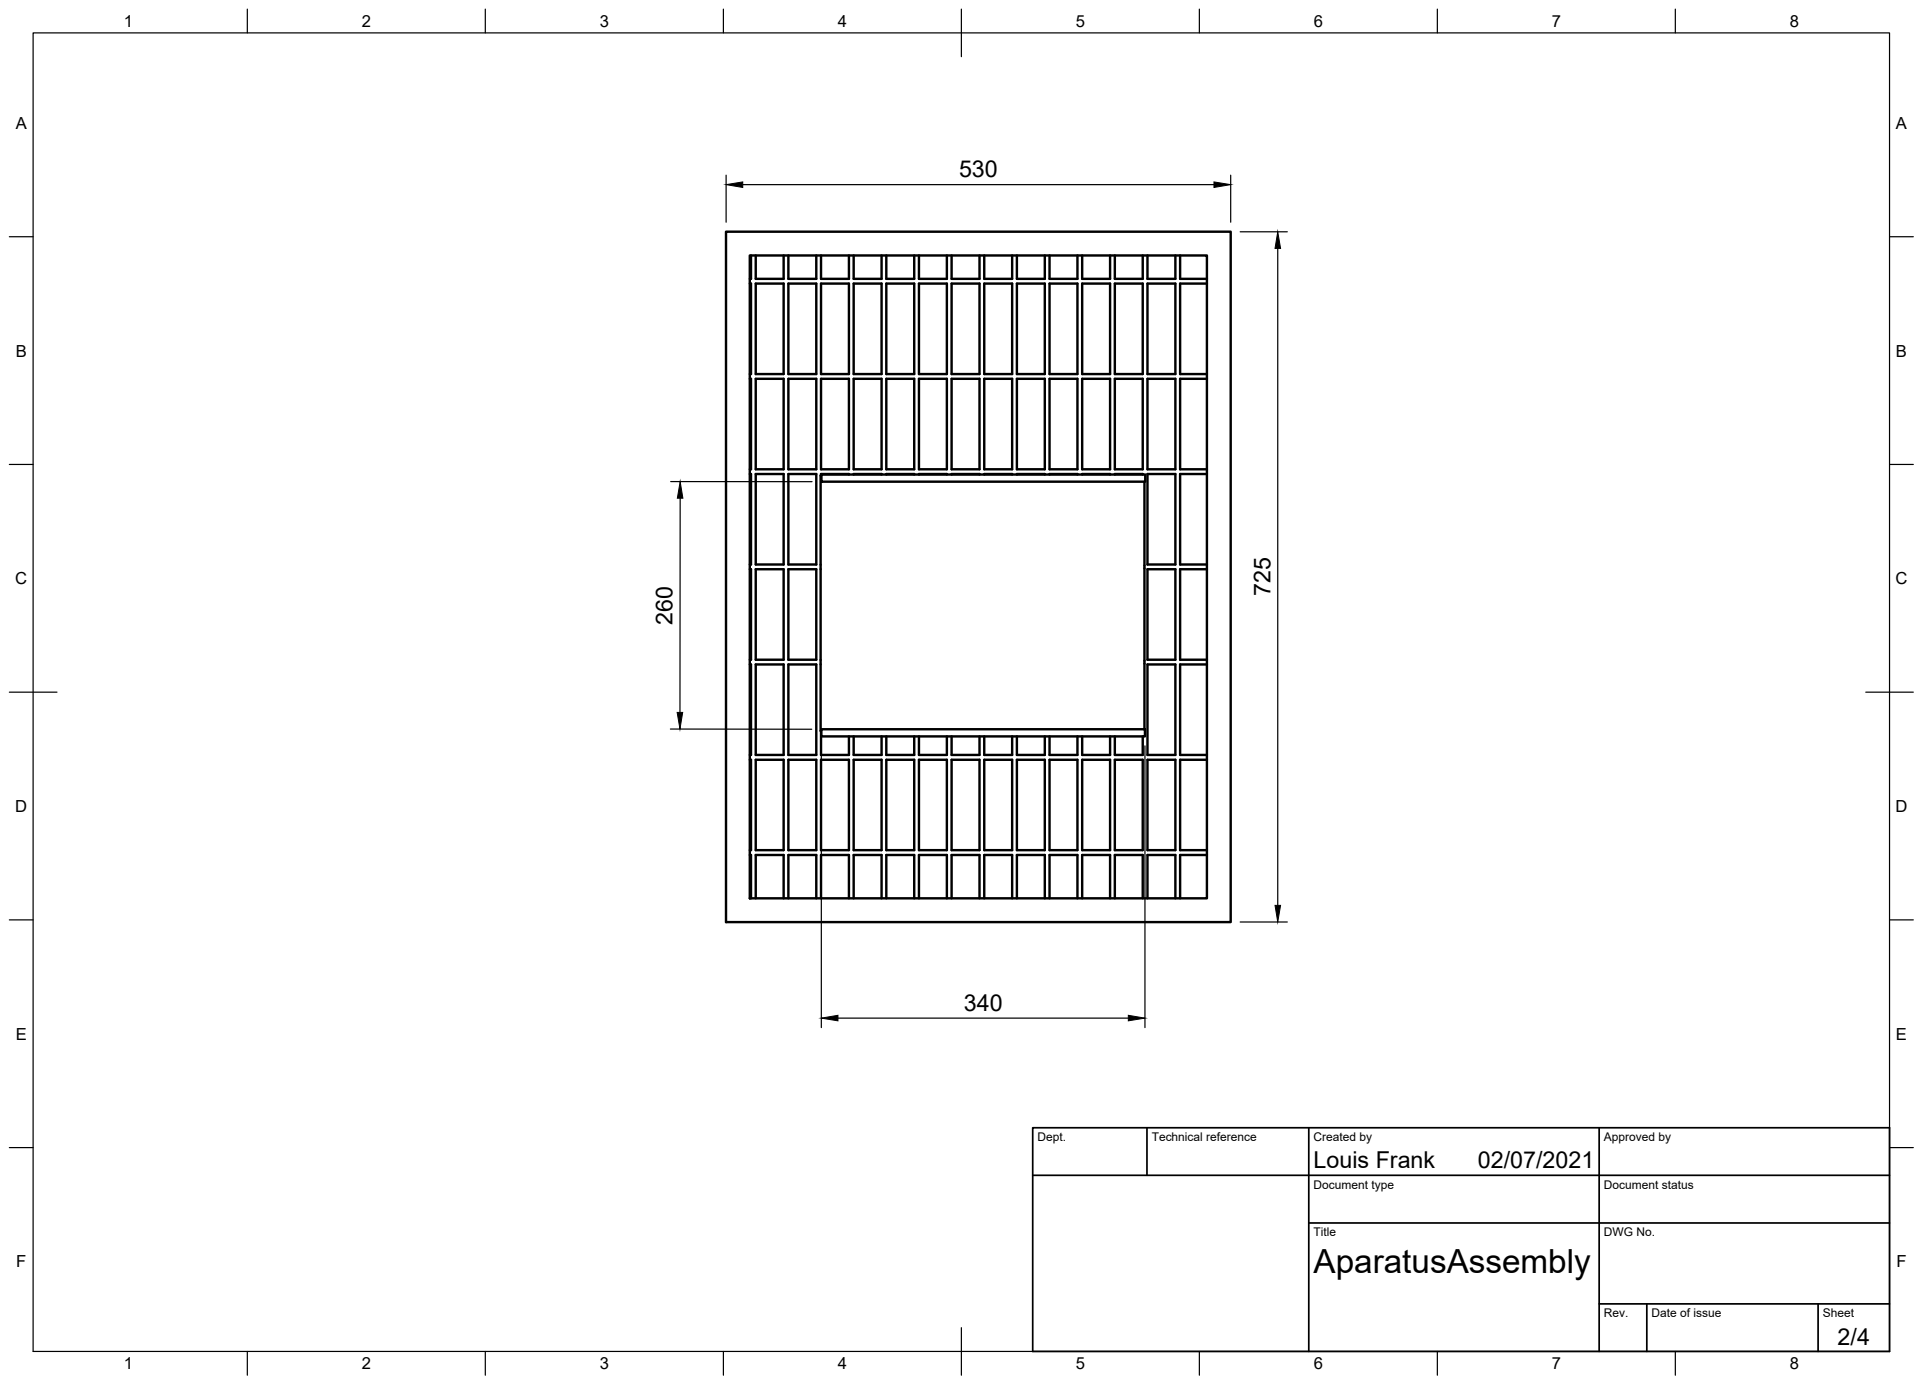
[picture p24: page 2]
Title; DWG No.

Dept. | Technical reference | Created by Louis Frank 02/07/2021 | Approved by

Document type | Document status

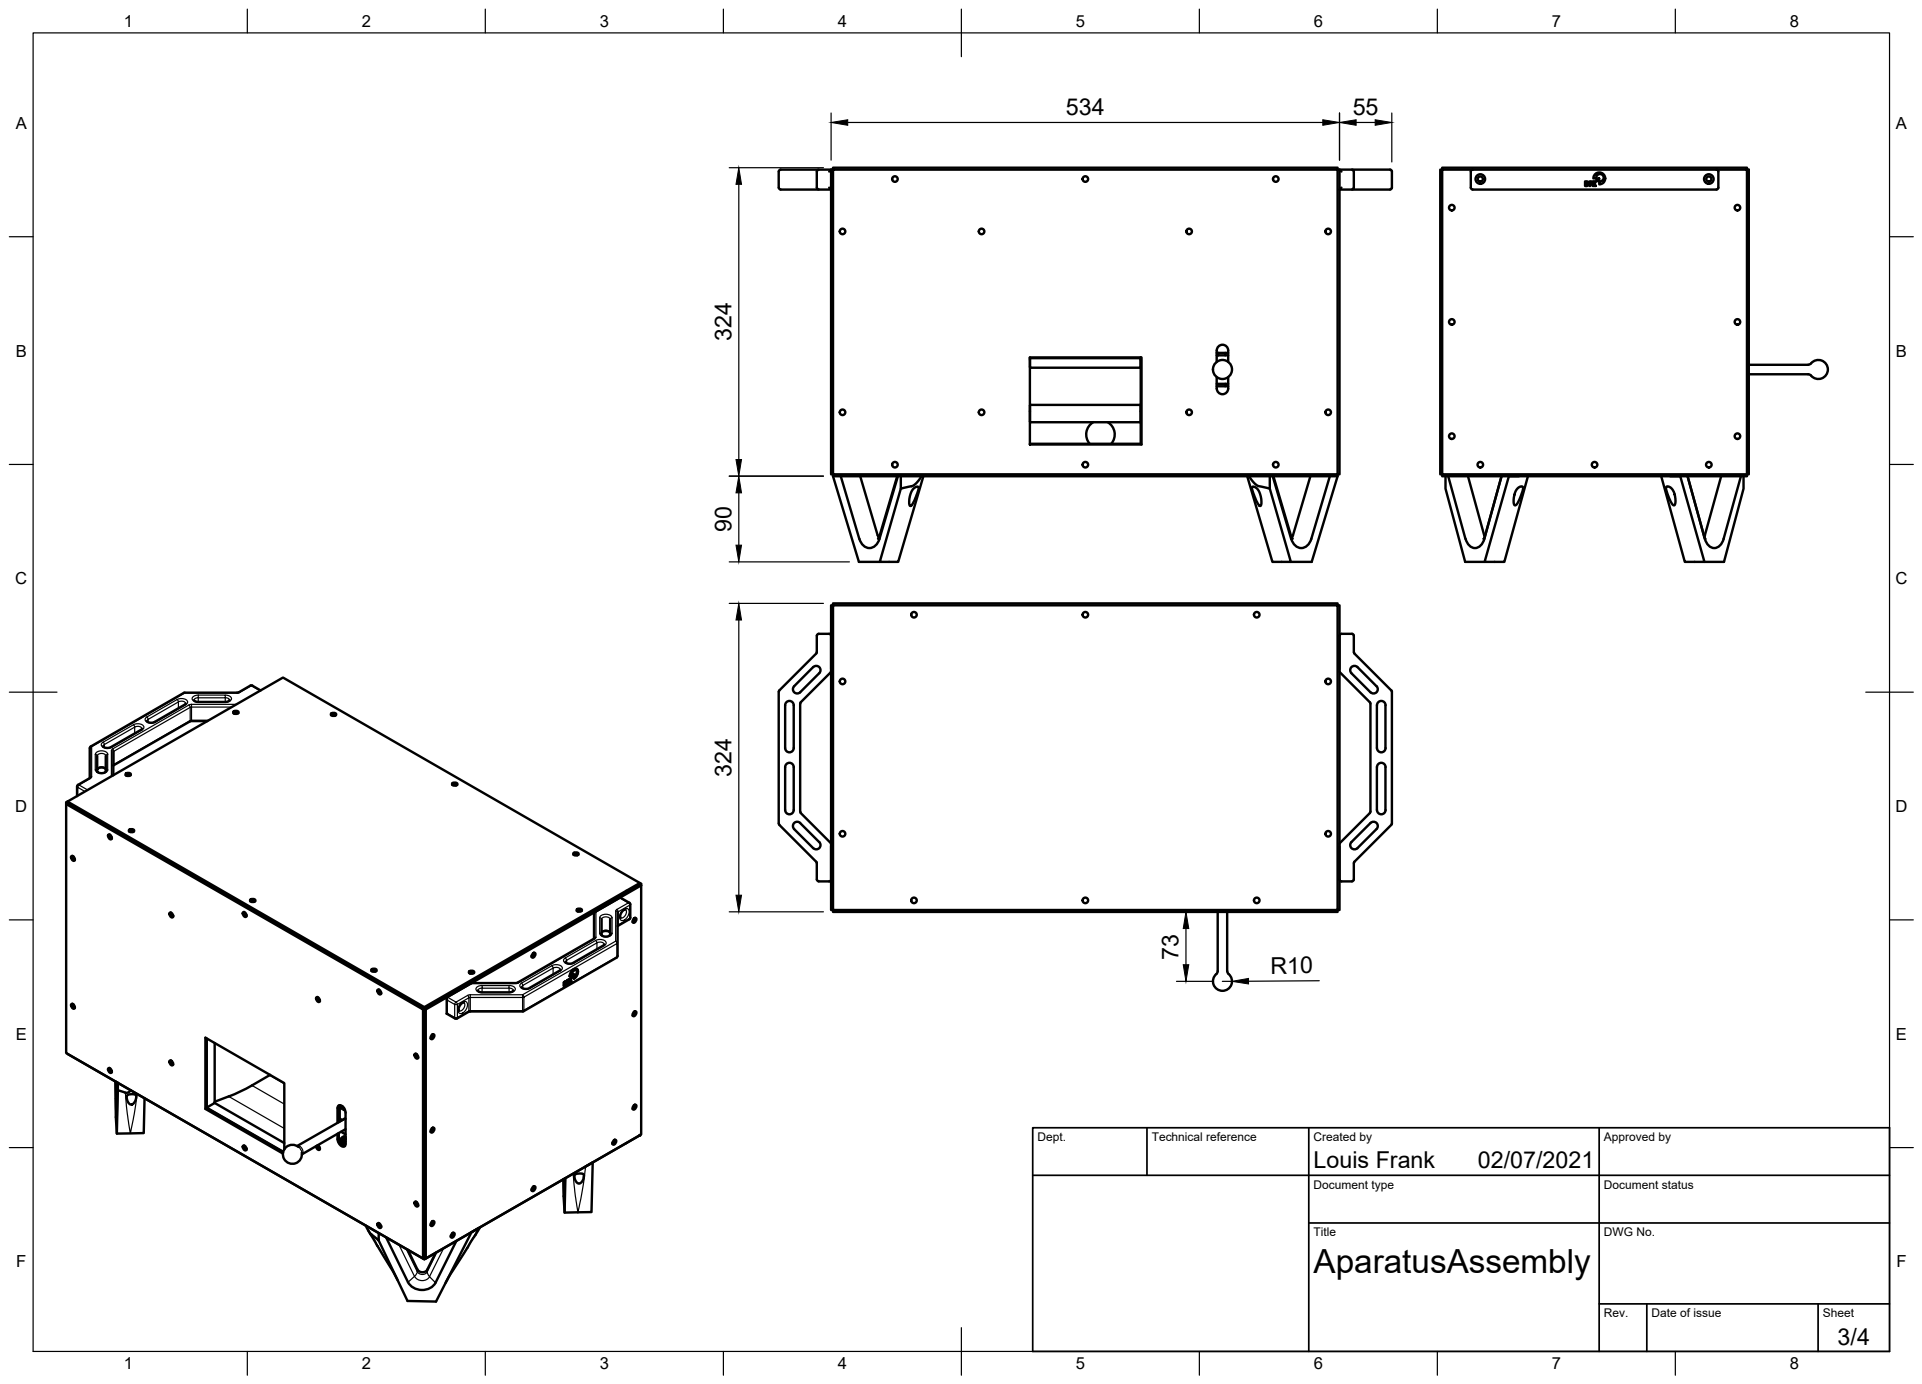
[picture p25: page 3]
Title; DWG No.; Louis Frank 324

Dept. | Technical reference | Created by 02/07/2021 | Approved by

Document type | Document status

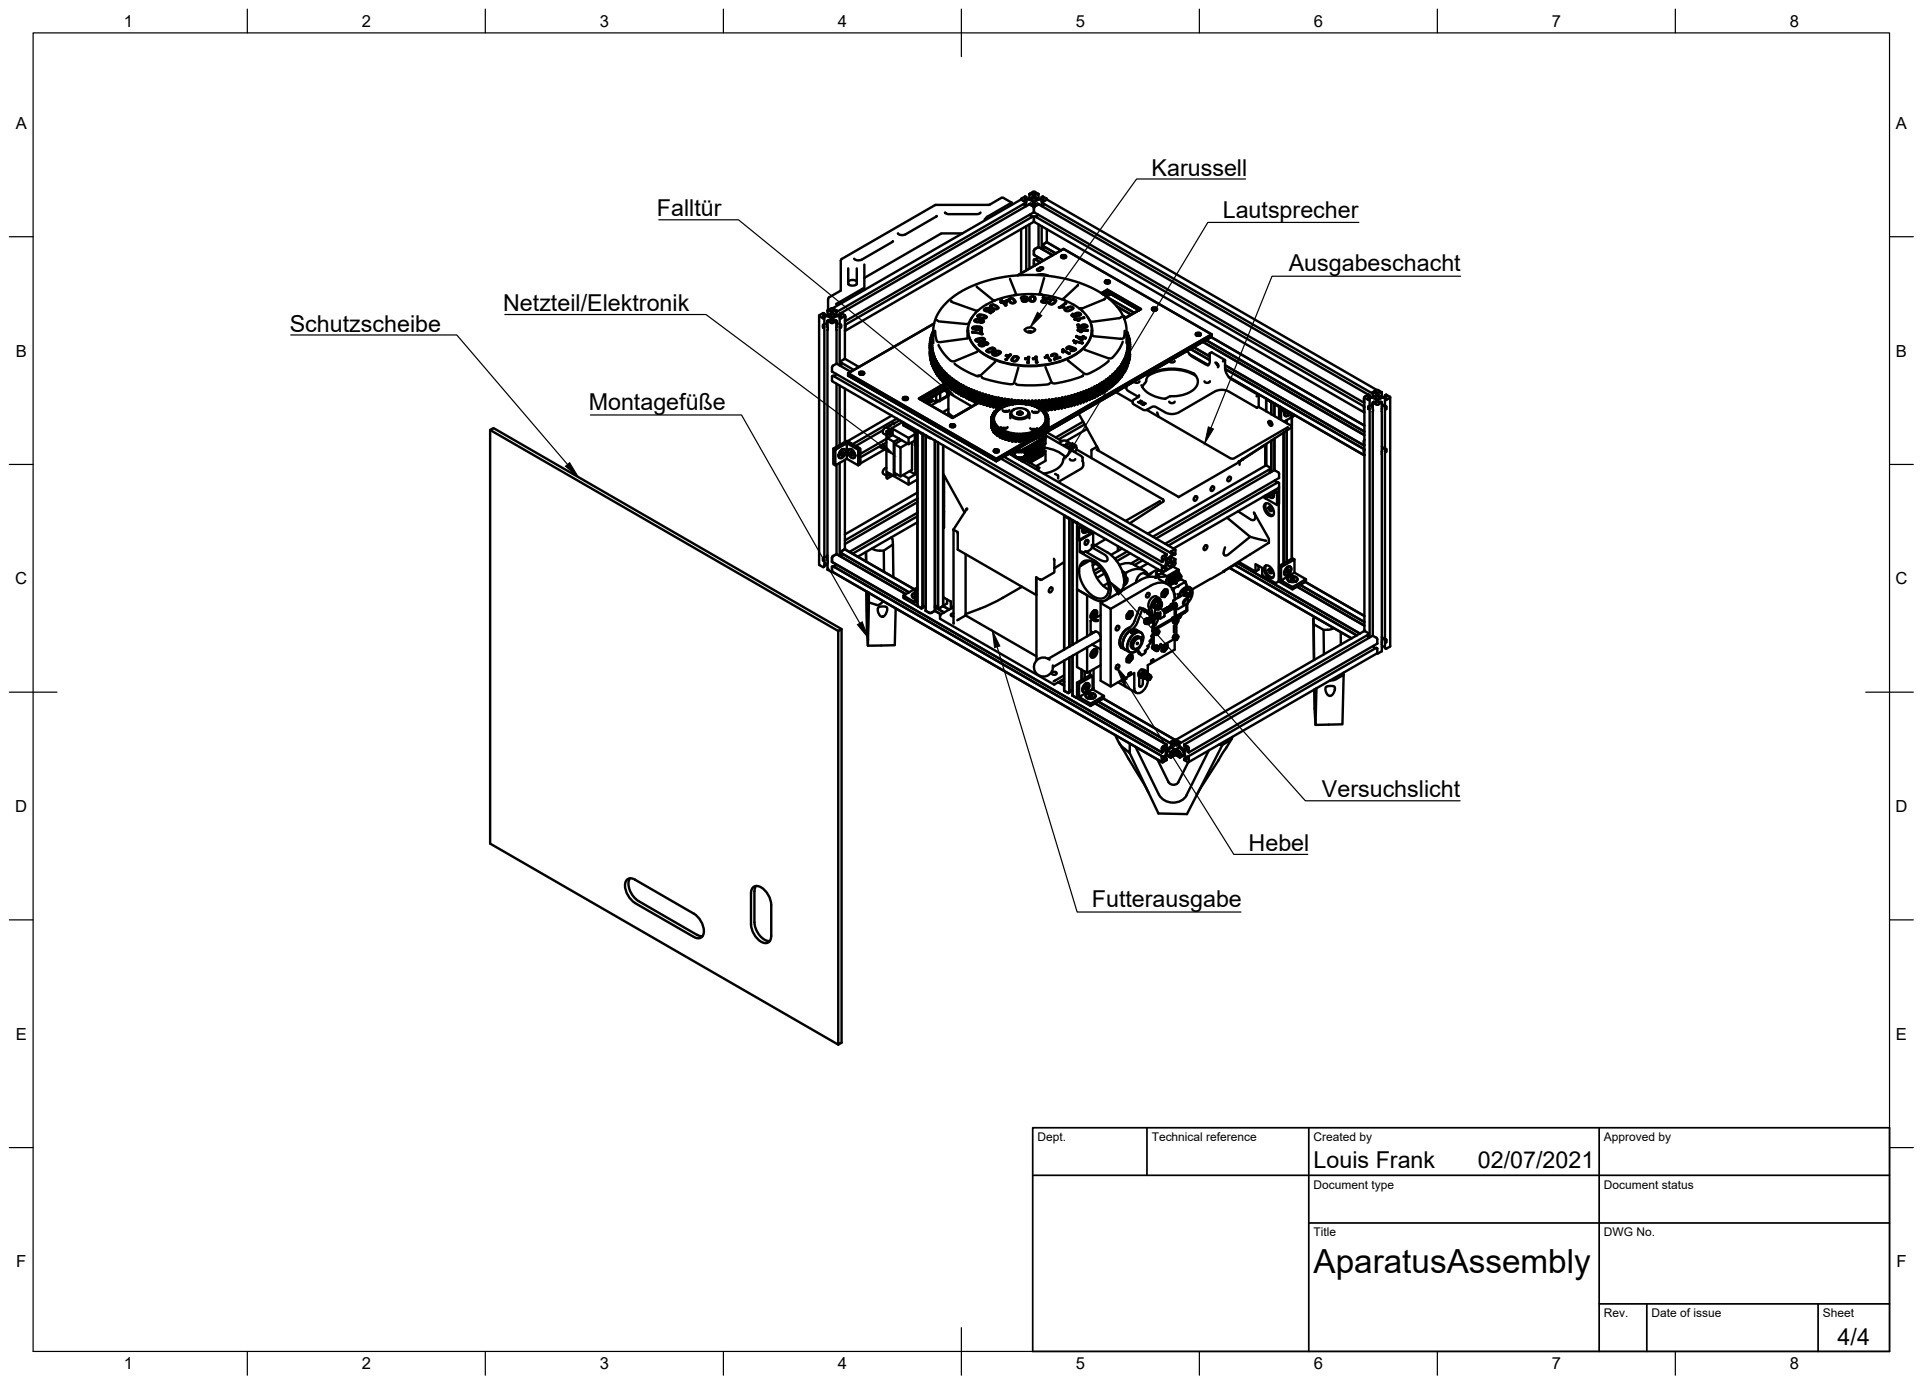
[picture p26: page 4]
Dept.; Technical reference; Created by; Approved by; Document type; Document status; Title; DWG No.; Louis Frank
